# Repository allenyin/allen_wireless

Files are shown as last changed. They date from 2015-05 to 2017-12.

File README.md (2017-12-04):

**Wireless Neural Recording System**

* [Overview](#Overview)
* [Hardware](#Hardware)
	* [Steps to convert old KiCad design files](#convertKiCad)
	* [Bridge](#Bridge-hw)
	* [Headstages](#headstages)
* [Firmware](#Firmware)
	* [Dependency](#Firmware-dependency)
	* [Bridge](#Bridge-fw)
	* [RHA-headstage](#RHA-fw)
	* [RHD-headstage](#RHD-fw)
		* [Firmware versions](#firmware-versions)
		* [JTAG testing](#JTAG-testing)
		* [Utility Programs](#Utility-programs)
* [Client Software](#gtkclient)
	* [Dependency](#gtkclient-dependency)
	* [Compilation](#gtkclient-compile)
    * [Running gtkclient](#running-gtkclient)
        * [RHA-headstage gtkclient](#RHAgtkclient)
        * [RHD-headstage gtkclient](#RHDgtkclient)
        * [Spike sorting](#SpikeSorting)
        * [Saving recordings](#SavingRecordings)
        * [Test recording](#TestRecording)
        * [Configuration files](#gtkclientConfigurations)
	* [TODO/possible improvements](#gtkclient-TODO)
* [Quick Start](#quickstart)

## <a name="Overview">Overview</a>
This project is modified from the multi-branch of the wireless neural recording system of the [myopen project](https://github.com/tlh24/myopen/tree/multi) by Tim Hanson.

As summarized in Hanson's [thesis](http://m8ta.com/tim/dissertation.pdf), the original system 

>consists of digitizing headstages, receiver/ethernet bridge, and PC client software. Each headstage has 4 32-channel Intan analog amplifiers, and ADCs to digitize the amplified signals. The amplifiers are connected to an onboard Blackfin DSP BF532 which performs automatic gain control, LMS adaptive noise cancellation, 8 poles of high and lowpass filtering, two templates comparison per channel, data compression, and pipelined radio control. The radio onboard transmits 1.3Mbps full filtered analog trace of four channels and threshold/template match for two units on all 128 channels. This is interleaved with 83kbps reception,which allows the client to edit parameters on the transceiver. The radio protocol allows any memory location to be changed on the headstage (specifically the blackfin), and the headstage streams can stream from any location in memory, with the memory address set by the PC client.

[32-channel Intan analog amplifiers](http://intantech.com/products_RHA2000.html)

[Blackin DSP BF532](http://www.analog.com/en/products/processors-dsp/blackfin/adsp-bf532.html)

The bridge, which is based around [Blackfin DSP BF537](http://www.analog.com/en/products/processors-dsp/blackfin/adsp-bf537.html), collects the wirelessly transmitted data from the headstages and send them to the PC client through ethernet.

<a name="figure_overview">*System overview, from Hanson's [thesis](http://m8ta.com/tim/dissertation.pdf)*</a>
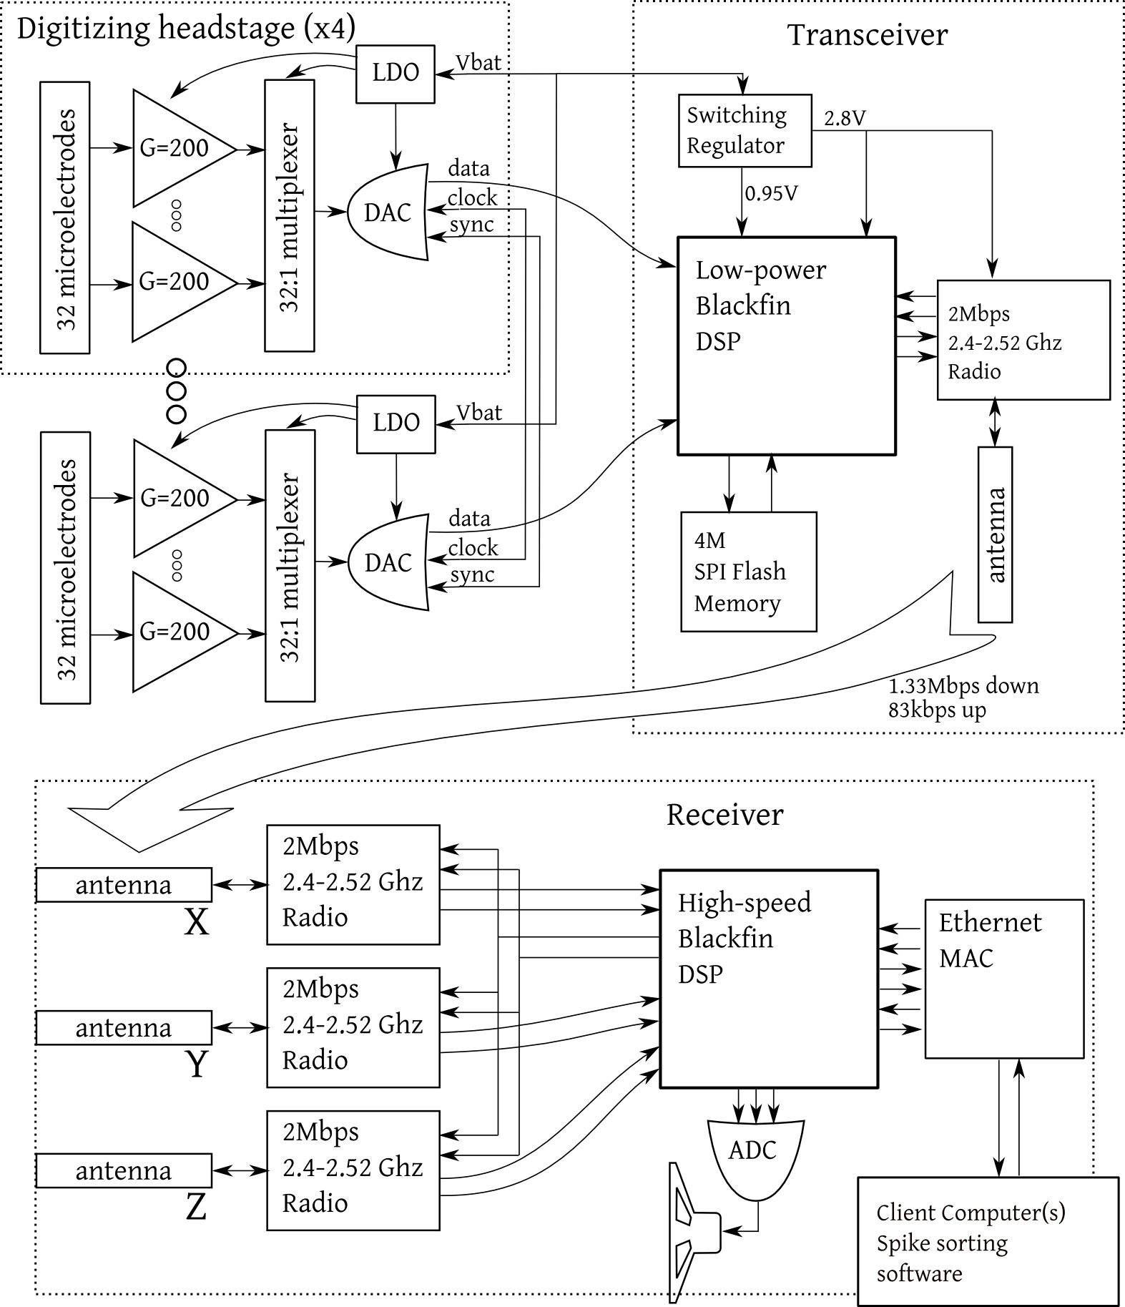
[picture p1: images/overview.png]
Hanson_Overview


This project modified the wireless headstage by replacing each of the 4 RHA2132 amplifiers, ADCs, and power converter chips with a single [32-channel RHD2132 digitizing amplifier](http://intantech.com/products_RHD2000.html). This is to reduce the power consumption and total area of the final PCB (by about 1/3). In terms of the figure above, this is equivalent of replacing the `G=200 and 32:1 multiplexer`, `ADC` and `LDO` components in the `Digitizing headstage` blocks by one component. 

In the rest of this document, the original headstages will be refered to as **RHA-headstage**, while the new design will be referred to as **RHD-headstage**. The client software will be referred to as **gtkclient**.

This document will describe:

* The overall hardware architecture of the headstages.
* Usage and setup for the bridge, headstage, and the PC client software.
* The different firmware versions used to develop and test the RHD-headstage.
* Debugging tools.

For technical details on the implementation, development, and troubleshooting of the firmware, see Tim's thesis, and the following development notes:

1. [Wireless Headstage: Blackfin BF532 headstage firmware setup](http://allenyin.github.io/reading_list/2016/01/BlackfinSetup)
2. [Wireless Headstage: Blackfin BF532 communication with Intan RHD2132 via SPI simulation via SPORT](http://allenyin.github.io/reading_list/2015/12/Blackfin-Intan-SPORT)
3. [Wireless Headstage: AGC with Blackfin BF532 and Intan RHD2132](http://allenyin.github.io/reading_list/2015/12/WirelessAGC)
4. [Wireless Headstage: Least-Mean Squared (LMS) adaptive noise cancellation](http://allenyin.github.io/reading_list/2016/01/BlackfinLMS)
5. [Wireless Headstage: Implementing direct-form I biquad IIR filters](http://allenyin.github.io/reading_list/2016/01/DirectFormI-IIR-butterworth-filters)
6. [Wireless Headstage: Generate oscillations by setting IIR coefficients](http://allenyin.github.io/reading_list/2016/01/IIRoscillator)
7. [Spike sorting via PCA and spike detection with SAA](http://allenyin.github.io/reading_list/2016/01/BlackfinSpikeSorting)
8. [Wireless Headstage: Radio transmission protocol between headstage and gtkclient](http://allenyin.github.io/reading_list/2016/01/BlackfinRadioTrans)
9. [Wireless Headstage: gtkclient notes](http://allenyin.github.io/reading_list/2016/01/gtkclient)

This repository contains the following folders:

* `bridge_hardware`: Ported from myopen's [stage10](https://github.com/tlh24/myopen/tree/master/emg_dsp/stage10). Components  stored in `bridge_library/`. Footprint archived to `bridge_library.pretty/` to use with newer version of `kicad (Version:0.201506030104+5696~23~ubuntu14.04.1-product,release build)`.

* `headstage_hardware`: Ported from myopen's [stage9](https://github.com/tlh24/myopen/tree/master/emg_dsp/stage9). Components stored in `headstage_library/`. Footprint archived to `headstage_library.pretty/` to use with newer version of kicad.

* `headstage2_hardware`: Modified from myopen's [stage9](https://github.com/tlh24/myopen/tree/master/emg_dsp/stage9). Uses 4xRHD2132 amplifiers rather than 4xRHA2132 amplifiers front-end. Eliminated separate ADCs and analog power-supply components.

* `myopen_multi`: Firmware and gtkclient software, which includes:
    * `bridge_firmware`: Same as myopen's [firmware_stage7](https://github.com/tlh24/myopen/tree/mutli/firmware_stage7).
    * `headstage_firmware`: Firmware for RHA-headstage. Port from myopen's [firmware_stage9_tmpl](https://github.com/tlh24/myopen/tree/multi/firmware_stage9_tmpl). Uses templates matching to transmit spike timings from the headstage.
    * `headstage2_firmware`: Firmware, development and debugging files for RHD-headstage.
    * `gtkclient_multi`: gtkclient source code adapted from myopen. Makefile modified to compile on Ubuntu14.04 and to support working with RHD-headstage's firmware.
    * `flasher`: Code used to write to the flash memories of the bridge and headstage through the parallel port.
    * `common_bfin`: Code common to all firmware and gtkclient.
    * `common_host`: Code common to the bridge firmware and gtkclient.
    * `algs`: Utilities need by gtkclient.
    
---
## <a name="Hardware">Hardware</a>

## <a name="convertKiCad">Steps to convert old KiCad design files</a>
The bridge and RHA-headstage PCB were designed with Tim's [kicadocaml](https://github.com/tlh24/kicadocaml), a variant of the opensource [KiCad](http://kicad-pcb.org/) PCB cad program. The design files were ported to KiCad, however the recent changes in KiCad's EESchema introduces some problems in using projects created with older version out of the box. Those impacts include:

0. Updated device library. The new device library footprints are smaller, this can cause older schematics to be displayed with broken connections. Solution: follow the procedures outlined [here](https://lists.launchpad.net/kicad-developers/msg17639.html) to use the rescue-lib.
0. Saving the old .brd files will convert them to .kicad_pcb. Subsequent openning of the board files will then result in parse errors and no board. Solution: Never save!!! (have not yet found a good solution).

In general, the KiCad files in `bridge_hardware/` and `headstage_hardware/` are for reference only, no save/modification should be needed.

The following steps were used to convert the old project files (example using `headstage_hardware/`):

0. Extract stage9 from `/emg_dsp`.
0. Create component and footprint library folders. `cd headstage_hardware; mkdir headstage_library headstage_library.pretty`
0. Open the schematic file, press OK for the rescue components dialog. Copy the cached component to our newly created library: `cp stage9-cache.lib headstage_library/headstage.lib`
0. Go to *Preferences*->*Component Libraries* and add headstage as an active library.
0. Ctrl-E on any of the component to open library editor. Set active library to be *headstage* and save component.
0. Close schematic and open again. Now editing any of the components in the library editor should show the active library as *headstage.lib*
0.  **Important! When closing the schematic, do not click on save!**
0. Open the .brd file, click ok on the resulting dialog.
0. Ctrl-E on any of the footprint to open the footprint editor. Click on *Create new library and save footprint* from the menu bar, and select the *headstage_library.pretty* folder to store the new library.
0. Go to *Preferences*->*Footprint libraries Wizard*->*Files on my computer* and select the *headstage_library.pretty* folder. This will add that directory to the footpring libraries available in this project. Make sure to select avaliable to project only.
0. *Select active library* in the footprint editor and make it *headstage_library.pretty*.
0. Close footprint editor and go back to the board. Go to *file*->*Archive Footprints*->*Create footprint archive* and select *headstage_library.pretty* as the library. Click yes to replace library. Now *headstage_library.pretty/* contains all the footprint used in the board as .mod files.
0. Make sure when footprint editor is opened, the active library is set correctly to the one we just created.
0. Again remeber to **NOT save the board file!!**
0. Open the schematic file and run Cvpcb to associate the components and the footprints in our own custom libraries. It's possible that a footprint is found in multiple libraries, chose to associate with the ones in *headstage*.

## <a name="Bridge-hw">Bridge</a>
As illustrated by the [Receiver block in the system overview](#figure_overview), the bridge mainly consists of three antenna-2.4GHz radio pairs for wireless communication, Blackfin DSP for processing, Ethernet/MAC chip for communication with gtkclient, and DAC (typo of DAC in Tim's thesis) for outputting received neural signals as audio.

In addition to wireless communication with the headstages, the bridge is also needed to program and debug the headstages.

<a name="bridge_labeled">*Bridge Board* </a>

labeled_bridge

In the above image:

A. Power switch.

B. USB power cable. 

C. Ethernet cable. Each operating headstage requires a bridge, requiring the PC on which gtkclient operates on to be connected to multiple bridges. Therefore, the ethernet port of the bridges and the client PC should all connect to the same switch or router.

D. Audio jack. When gtkclient is running, connecting the bridge to an audio device allows the user to hear the the 4 selected channels in gtkclient.

E. Blackfin BF537 DSP processor.

F. JTAG header pins for debugging the bridge. The pin missing on the top row ensures correct orientation of the JTAG in-circuit emulator (ICE).

G. Header pins for writing firmware to the bridge's flash memory. See [bridge flashing instructions](#Bridge-fw).

H. Indicator LED lights. After power on, these LEDs would fluctuate. Normal operation is indicated by the LEDs lit up in the image lighting up. Except for the bottom most one, which should be blinking periodically.

I. Header pins for writing firmware to the headstage's flash memory. See [RHA-flashing instructions](#RHA-fw) and [RHD-flashing instructions](#RHD-fw).

J. Omnetics connector for writing firmware to the headstage's flash memory. The signals applied to the column of header pins above it are applied to the headstage through this connection to the corresponding omnetics connector on the headstage.

K. JTAG header pins for debugging the headstage. The pin missing on the left column ensures correct orientation of JTAG ICE. See [RHD firmware testing](#JTAG-testing).

L. Omnetics connector for JTAG debugging the headstage. The signals applied to the JTAG header pins are passed to the headstage through this connection.

M. 2.4GHz Nordic radio and antenna pairs. Having three antenna allow for spatial reception diversity and enable better wireless signal quality.

**Parallel Port Flash Cable**

A 25-pins [IBM PC-comptabile parallel port](https://en.wikipedia.org/wiki/Parallel_port#Pinouts) cable is modified to use for the flashing process, see [firmware section](#Firmware) for instructions.  The unmodified end of the DB25 cable is connected to the parallel port, while the modified end connects to the 7-pin header connectors on the bridge, labeled G and I above.

The flash cable on one end needs to be modified as shown below:

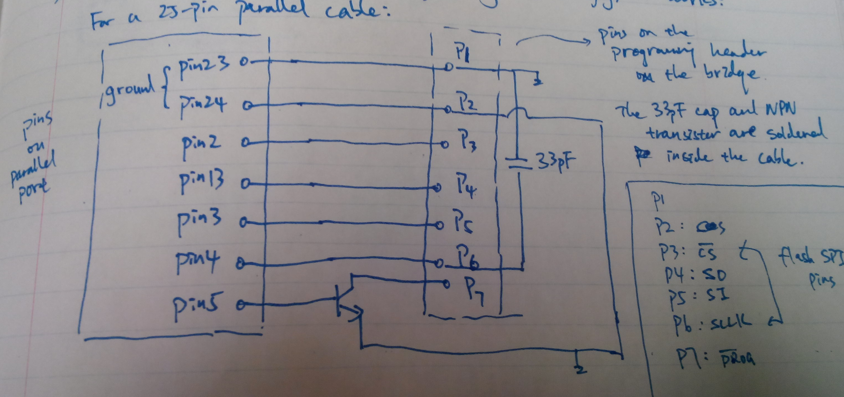
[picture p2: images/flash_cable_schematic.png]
flash_cable
<a name="flash_cable">*Flash Cable Schematic*</a>

The left box shows the relevant pins on the unmodified DB25 connector, the right box shows the corresponding header pins on the bridge. There needs to be a `33pF` capacitor connecting `pin23` and `pin4` of the parallel cable. `pin5` of the cable needs to connect to the base of an NPN transistor, whose emmiter is connected to ground via either `pin23` or `pin24`, while the collector goes to `pin7` of the bridge headers.

Specifically, the parallel port to SPI correspondence is:

* `pin2` = `_CS` -- chip select of the SPI flash memory.
* `pin13` = `SO` -- the input of the parallel port is connected to the output (SO) of the flash memory.
* `pin3` = `SI` -- the output of the parallel port is connected to the input (SI) of the flash memory.
* `pin4` = `SCLK` -- serial clock (SCLK) of the flash memory.

`pin5` is not part of the 4-line SPI interface, but it is used to allow the line-driver onboard the bridge to select the flash memory to use the SPI bus. This is necessary since the SPI bus on the Blackfins of both the bridge and headstage is shared between the flash memory and the radio chip.

The modified flash cable will include the capacitor and the NPN transistor. The polarity of the 7-pin connector can be figured out by probing to see which pin is grounded onboard the bridge.

## <a name="headstages">Headstages</a>

In image below, the fully assembled RHA-headstage is on the left. The RHD-headstage is on the right.

<a name="headstages_labeled">*Headstage PCBs*</a>

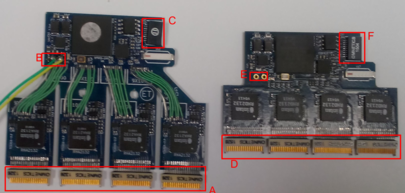
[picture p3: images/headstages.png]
labeled_headstages labled_headstages


Labeled in the image are the connectors the headstages can make:

A. RHA-headstage Omnetics connectors to electrodes. Each of the four connectors has two rows of 20 pins each. The leftmost and rightmost pins of each row are guide posts and connect no signals. The second leftmost and the second rightmost pins of each row are the reference electrodes.

B. RHA-headstage power connection to 3.7V battery.

C. RHA-headstage Omnetics connector for flashing memory. The JTAG debugging connector is on the back side of the board at the same location.

D. RHD-headstage Omnetics connectors to electrodes. Exactly the same as the RHA-headstage.

E. RHD-headstage power connection to 3.7V battery. Connection not installed in the pictre.

F. RHD-headstage Omnetics connector for flashing memory. The JTAG debugging connector is on the back side of the board at the same location.

The bottom half of both headstages are the `digitizing headstages` block in the [System overview diagram](#figure_overview), which is where the headstages differ hardware-wise. The top halves are the `transceiver block` and are identical.

While the electrodes for both headstages are identical, the electrode-to-amplifier connections are different. Below are the electrode-to-channel mapping for each headstage, containing only the 32 signal-carrying electrodes of the connector (excluding the guide posts). Note that each amplifier is connected to one group of 32 electrodes.

*RHA-headstage electrode-to-channel mapping, ordered from left-to-right*

top-row|31|30|29|28|27|26|25|24|23|22|21|20|19|18|17|16|
-------|---|---|---|---|---|---|---|---|---|---|---|---|---|---|---|---|
bot-row|15|14|13|12|11|10| 9| 8| 7| 6| 5| 4| 3| 2| 1| 0|

*RHD-headstage electrode-to-channel mapping, ordered from left-to-right*

top-row|23|22|21|20|19|18|17|16|15|14|13|12|11|10|9|8|
-------|---|---|---|---|---|---|---|---|---|---|---|---|---|---|---|---|
bot-row|24|25|26|27|28|29|30|31|0|1|2|3|4|5|6|7|

## <a name="Firmware">Firmware</a>
The firmware is written in a combination of C and Blackfin assembly language. While Analog Devices (ADI) provides its own software development toolchains, it requires purchasing a pretty expensive license (though it comes with a lot more support). For the myopen and this project, the open source gnu gcc blackfin toolchain is used. Further, all development was done on debian based OS. The Makefiles in this repository are tested only in Ubuntu 14.04. Minor adjustments might be needed to work on other debian-based OS.

## <a name="Firmware-dependency">Dependency</a>

Compiling the firmware requires the [Blackfin Toolchain in Linux for Bare Metal](https://blackfin.uclinux.org/doku.php?id=toolchain:installing). For debian-based linux OS:

* Download the latest version, as of June, 2015, it's `blackfin-toolchain-elf-gcc-4.3-2014R1-RC2.x86_64.tar.bz2`
* Extract and move to `/opt`
* Add path to `/opt/uClinux/bfin-elf/bin` to the `PATH` variable through `.bashrc`

Two must-have references to understand Blackfin architecture:

* [ADSP-BF5xx/ADSP-BF60x Blackfin Processor Programming Reference](http://www.analog.com/media/en/dsp-documentation/processor-manuals/Blackfin_pgr_rev2.2.pdf), describes all assembly commands and options.
* [ADSP-BF533 Blackfin Processor Hardware Reference](http://www.analog.com/media/en/dsp-documentation/processor-manuals/ADSP-BF533_hwr_rev3.6.pdf), describes all components and functions of the processor.  BF533 processor is mostly identical with BF532, which are the processors onboard the headstages. For the bridge, see BF537.

After compiling the firmware, the binary needs to be uploaded into the SPI flash memory onboard the bridge or headstage. This is done through a parallel port (for speed and relative ease). There are two ways this could be done.

**Using Libparapin**

In older computers with integrated parallel port (such as our lab's `rabbit` running DebianWheezy), [libparapin](http://parapin.sourceforge.net) can be installed to talk to the paralle port. This was used by Tim to develop and flash the RHA-headstages.

After installation of libparapin (in either user or kernel mode), compile `myopen_multi/flasher/flash.c` with `make clean; make`. 

With proper PC-to-bridge (and bridge-to-headstage) connections, compiled firmware binary can be uploaded with `sudo ./flash myprogram.ldr`.

**Using Pyparallel (recommended)**

Unfortunately Libparapin does not play nicely with parallel port PCI expansion cards and/or newer OS. I'm not sure what the exact culprit is, but the most recent version of libparapin is for kernel version2.6, and there hasn't been any activity on the project in several years.

Fortunately the python library [pyparallel](https://github.com/pyserial/pyparallel), allows us to interact with the parallel conveniently. Note that `pyparallel` can also refer to a Python parallel processing package. See [Lewis Loflin's blog posts](http://www.bristolwatch.com/pport/index.htm) for details on using the library.

After installing this module, firmware can be flashed with `python flash.py myprogram.ldr`. Error might occur indicating parallel port cannot be openened, in which case do `sudo rmmod lp; sudo modprobe ppdev` and try again.

Successful flash message:
```
python ../flasher/flash.py stage.ldr
ldr file: stage.ldr
File size 12202 bytes, 48 pages.

Requesting manufacturer opcode...

Read: 0xbf 

Looks like microchip flash.
Read: 0xbf 

Read: 0x25 

Read: 0x8d 

Read: 0xbf 

Detected: 
SST25VF040
SST25 sanity check ok.
Status register 0x0
Bank protect bits = read-write.
AAI off.
Block protect off.
Device is not write enabled. (default)
Device is ready.
Erasing SST25!
Waiting for the erase to complete..
Status register 0x0
Bank protect bits = read-write.
AAI off.
Block protect off.
Device is not write enabled. (default)
Device is ready.
write_all2_SST25 writing buffer length 12202
Verifying all..
 ok.

All pages verified correctly! :)
```
## <a name="Bridge-fw">Bridge</a>

The bridge firmware was not modified from the original myopen project (except the Makefile, for directory consistency). To flash the bridge, connect the flash cable to the bridge header pins as below, note the direction of cable connection is marked on the red flash cable.

<a name="Bridgeflash">*Flashing the bridge*</a>
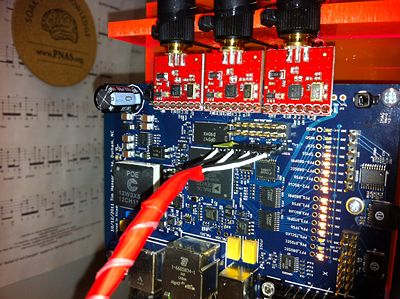
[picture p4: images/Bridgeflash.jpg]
Bridgeflash


1. Go to the `myopen_multi/bridge_firmware/` directory, and do `make clean; make` to compile the firmware. 

	Note that each bridge is receives from a different headstage. Therefore, if multiple headstages are used, multiple bridges will need to be flashed and used. 

	If multiple briges are used, make sure the MAC addresses for the bridges are different. Go to `myopen_multi/common_bfin/ethernet.c`, in function `SetupMacAddr()`, change the value of `MACaddr[5]` so that the bridges used have different values.

2. Turn the bridge on, making sure the USB power cable is connected, then do `make flash`. 
 
	`make flash` will use either the libparapin based `flash.c` or pyparallel based `flash.py` to write the firmware to memory, based on what option is enabled in the Makefile under the `flash` rule. The default option will use the Python method.

## <a name="RHA-fw">RHA-headstage</a>

The RHA-headstage firmware was not modified from the original myopen project (except the Makefile, for directory consistency). To flash the heastage, connect the flash cable to the bridge header pins, and the 9-pins Omnetics cable to the bridge as shown below, note the direction of cable connection is marked on the red flash cable.

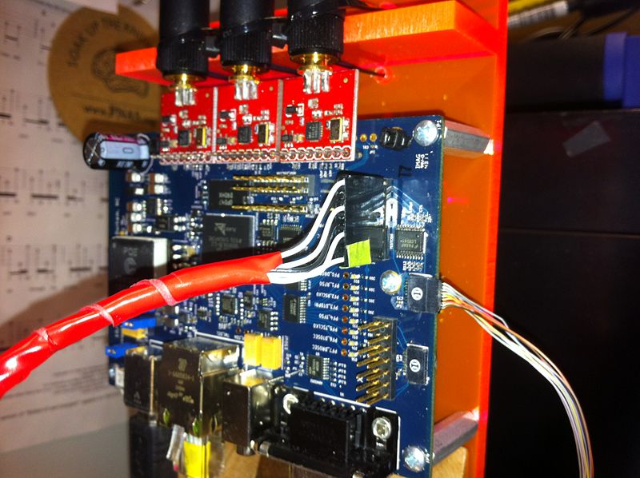
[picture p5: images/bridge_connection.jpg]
bridge_connection
<a name="bridge_connection">*Bridge connection to flash headstage*</a>

1. Connect the other end of the 9-pins cable to the top-side omnetics connector on the headstage as shown below, note that the top wire on the bridge is also the top wire on the headstage.

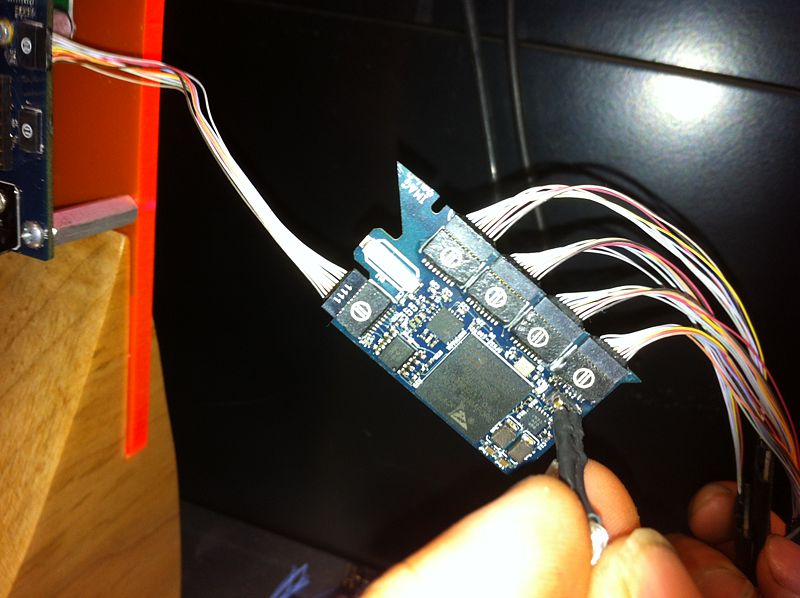
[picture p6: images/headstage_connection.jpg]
headstage_connection
	<a name="headstage_connection">*RHA-headstage connection*</a>

	Note that the RHA-headstage shown in the image is only the transceiver top half.

2. Go to the `myopen_multi/headstage_firmware/` directory, and do `make clean; make` to compile the firmware.

	Note that if multiple headstages are used, they must be configured to operate on different radio frequency. To change the radio channel, go to `myopen_multi/headstage_firmware/main.c` and search for the call to `radio_init()` and change the input argument. An input value of `84`, for example, sets the radio to operate on `2400MHz + 84Hz = 2484Mhz`. Other possible values are 94, 114, and 124. The maximum is 124. These changes must be followed by firmware recompilation.

    Theoretically, the 2.4GHz radio used onboard can operate with 2Msps on 62 different 2MHz bandwidth channels. The radio can operate from 2.4GHz to 2.525Ghz. When operating at 2Msps, each frequency requires a 2MHz bandwidth. Therefore, with no overlap, the input value to `radio_init()` can take values of 0, 2, 4,..., 124. However, the lower frequency bands are prone to attenuation by water absoprtion and interference from WiFi/Bluetooth/ZigBee bands. Therefore, the actual frequencies used should be limited to the higher bands. When multiple headstages are used, they should be set at frequencies as far apart as possible (note the separation of 10-20MHz for the values suggested).

    See [Nordic nRF24L01 manual section6.3](http://www.nordicsemi.com/eng/content/download/2730/34105/file/nRF24L01_Product_Specification_v2_0.pdf).

3. Turn on the bridge, and flash the headstage with `make flash`. 

	`make flash` will use either the libparapin based `flash.c` or pyparallel based `flash.py` to write the firmware to memory, based on what option is enabled in the Makefile under the `flash` rule. The default option will use the Python method.

4. Modify gtkclient:
 	* Make sure in `myopen_multi/gtkclient_multi/Makefile`, the option `HEADSTAGE_TIM` is set to `TRUE`, while setting `RADIO_BASIC`, `RADIO_AGC`, `RADIO_AGC_IIR` and `RADIO_AGC_IIR_SAA` to `false`.
	* Go to `myopen_multi/gtkclient_multi/src/gtkclient.cpp` and make sure the radio channel given to `radio_init()` in the headstage's firmware is present in the array `g_radioChannel`. 
	* If using multiple headstage-bridge pairs for recording, make sure the value of `NSCALE` defined in `myopen_multi/gtkclient_multi/include/gtkclient.h` is set to the number of headstage-bridge pairs used.
   
    After all (if any) gtkclient modifications, recompile gtkclient by navigating into `myopen_multi/gtkclient_multi` and type `make clean; make`. gtkclient is now ready to be used with RHA-headstages.

When powered on, the LED onboard should blink periodically.

The file `memory_map.ods` is a spreadsheet visualizing the memory organization used in the RHA-headstage firmware.

## <a name="RHD-fw">RHD-headstage</a>

The parallel port-to-bridge connections and bridge-to-headstage connections are identical for RHD-headstage as for RHA-headstages. However, there are multiple firmwares available in the `myopen_multi/headstage2_firmware` directory. To program the RHD-headstage to use the final firmware version -- `radio_gain_IIR_SAA.asm`, navigate to that directory and:

1. Uncomment the line `FIRMWARE_VERSION=radio_gain_IIR_SAA` line in `myopen_multi/headstage2_firmware/Makefile`.

2. Type `make clean; make` to compile the firmware.

	Note that if multiple headstages are used, they must be configured to operate on different radio frequency. To change the radio channel, go to `myopen_multi/headstage_firmware/main.c` and search for the call to `radio_init()` and change the input argument. An input value of `84`, for example, sets the radio to operate on `2400MHz + 84Hz = 2484Mhz`. Other possible values are 94, 114, and 124. The maximum is 124. These changes must be followed by firmware recompilation.

    Theoretically, the 2.4GHz radio used onboard can operate with 2Msps on 62 different 2MHz bandwidth channels. The radio can operate from 2.4GHz to 2.525Ghz. When operating at 2Msps, each frequency requires a 2MHz bandwidth. Therefore, with no overlap, the input value to `radio_init()` can take values of 0, 2, 4,..., 124. However, the lower frequency bands are prone to attenuation by water absoprtion and interference from WiFi/Bluetooth/ZigBee bands. Therefore, the actual frequencies used should be limited to the higher bands. When multiple headstages are used, they should be set at frequencies as far apart as possible (note the separation of 10-20MHz for the values suggested).
	
    See [Nordic nRF24L01 manual section6.3](http://www.nordicsemi.com/eng/content/download/2730/34105/file/nRF24L01_Product_Specification_v2_0.pdf).

3.  Turn on the bridge and do `make flash`. 

	There should be a line in the output message that says `FIRMWARE_VERSION is RADIO_GAIN_IIR_SAA`. If not, make sure again in Makefile that all other lines containing `FIMRWARE_VERSION=` is commented out.

4. Modify gtkclient:
	* Go to `myopen_multi/gtkclient_multi/Makefile` and set the option `RADIO_GAIN_IIR_SAA` to true, while setting `HEADSTAGE_TIM`, `RADIO_BASIC`, `RADIO_AGC`, `RADIO_AGC_IIR`, `RADIO_AGC_IIR_SAA` to `false`. This ensures gtkclient can correctly communicate with the RHD-headstage firmware.
	* Go to `myopen_multi/gtkclient_multi/src/gtkclient.cpp` and make sure the radio channel given to `radio_init()` in the headstage's firmware is present in the array `g_radioChannel`.
	* If using multiple headstage-bridge pairs for recording, make sure the value of `NSCALE` defined in `myopen_multi/gtkclient_multi/include/gtkclient.h` is set to the number of headstage-bridge pairs used.

	After all (if any) gtkclient modifications, recompile gtkclient inside `myopen_multi/gtkclient_multi` directory with `make clean; make` -- gtkclient is now ready to be used with RHD-headstage.

When turned on, the onboard LED should blink periodically.

## <a name="firmware-versions">Firmware versions</a> ##
There are other firmware version in this directory, many of them were used in the process and developing
the final firmware.

* `intan_setup_test.asm`:  

    Polls the same channel from all 4 Intan amplifiers, and save periods to memory starting at FP_BASE (0xFF906F00). Plot the result using `plot_memdump.py`, function `within_amp()`. Used to find optimal setup for the RHD amplifiers.

    Compile and flash with `make clean; make; make flash` after uncommenting `FIRMWARE_VERSION=intan_setup_test` and commenting out all other `FIRMWARE_VERSION` comments. Does not use the radio so not supported by gtkclient.

    The blackfin cache memory organization can be visualized by the spreadsheet `Intan_setup.ods`. Memory header is `memory_RHA.h` -- identical to RHA-headstage's `memory.h` file.

* `intan_setup_test2.asm`: 

    Tests the intra-amp performance. Records a set number of periods from all 32 channels of a fixed amp (see comments in file), save to memory in A1 (0xFF904000). Results include Intan-setup responses. Use `plot_memdump.py`, function `within_amp()` to plot the results.

    Compile and flash with `make clean; make; make flash` after uncommenting `FIRMWARE_VERSION=intan_setup_test2` and commenting out all other `FIMRWARE_VERSION` comments. Does not use the radio, not supported by gtkclient.

    The blackfin cache memory organization can be visualized by the spreadsheet `Intan_setup.ods` Memory header is `memory_RHA.h` -- identical to RHA-headstage's `memory.h` file.

* `firmware1.asm`:
   
    Integrated intan_test_setup2 into the firmware structure...after the setup process, repeatedly poll all the SPORT, but saves all channels from just one amp to WF_BUF. This allows for 256 32-bit words, which is equivalent to getting 16 samples from all 32-channels of the designated amplifier. 

    After saving the samples, part of the signal chain (AGC+IIR+SAA) was used to see how much code-path can be fit in before data corruption happens. The data in WFBUF can be dumped after it's full and plotted with `plot_packet_samples.py` (`plot_packet('bla.txt', 16, 32)`). Contains no radio code. Not supported by gtkclient.

    Memory header is `memory_RHA.h` -- identical to RHA-headstage's `memory.h` file.

* `firmware2.asm`:

    Same as `firmware1.asm`, except the extra signal path code is replaced with nops to investiage code-length issues.

* `radio_basic.asm`:

    Built off firmware2.asm, but integrate in radio communication with gtkclient. The radio communication involved is a stripped-down version of the original radio protocol -- writes in the raw samples, but since no spike-sorting is done, the matching bits are simply set to 0. Instructions to add in the echo nibble and packet#-in-frame nibble are present, so gtkclient can correctly read and interpret the packet information. 
                 
    Requires uncommenting the `FIRMWARE_VERSION=radio_basic` in makefile to compile, uses the "memory_radio_basic.h" file, which describes the memory layout. The memory header file is taken care of by the Makefile. The corresponding header will be moved to be "memory.h" when the `FIMRWARE_VERSION` option is set.

    The blackfin cache memory organization can be visualized by the spreadsheet `radio_basic_memoryMap.ods`.

    To use with gtkclient, compile gtkclient with `RADIO_BASIC` set to true in the Makefile. 

    While running gtkclient, since no matches are actually made, in the spike-window, the waveforms may be colored blue and messages in stdin about false-positivies can happen. This is normal and safe to ignore.

* `radio_AGC.asm`:

    Built off radio_basic.asm, but with added AGC functions. Same radio-communication protocol as in radio_basic. Compile with `FIMRWARE_VERSION=radio_AGC`, use "memory_AGC.h". 

    The blackfin cache memory organization can be visualized by the spreadsheet `radio_AGC_memoryMap.ods`.

    To use with gtkclient, compile gtkclient with `RADIO_AGC` set to true in its Makefile. Same spike false-positives will occur.

* `radio_AGC_IIR.asm`:

    Built off radio_AGC.asm, but added two IIR biquads to act as band-pass filter, set to [250, 9000Hz]. Compile with `FIMRWARE_VERSION=radio_AGC_IIR`, use "memory_AGC_IIR.h".

    The blackfin cache memory organization can be visualized by the spreadsheet `radio_AGC_IIR_memoryMap.ods`.

    To use with gtkclient, compile gtkclient with `RADIO_AGC_IIR` set to true in its Makefile. Same spike false-positives will occur.
                   
    <s>Note that unlike the original gtkclient, this version will not have an option to set the gain. This is because previously the samples were 12-bits, with Q16 values, the IIR may adjust its coefficients to apply a gain of up to 2 on its incoming samples, this is the mechanism through which Tim's gtkclient applies the gain. In the RHD version of headstage, the incoming samples are already 16-bits, therefore no gain needs/should be applied.</s> 
    
    The `IIR-gain` field allows an extra gain to be applied via the low-pass biquad. In practice, this should limitied between [-2.5, 2.5]. See [Wireless Headstage: Implementing direct-form I biquad IIR filters](http://allenyin.github.io/reading_list/2016/01/DirectFormI-IIR-butterworth-filters) for details. This is the case for all RHD firmware containing AGC and IIR stages.
                   
    By changing the IIR-biquad coefficients, oscillations of different frequency may be introduced. The `osc` radio button in this version of gtkclient does this. Clicking that radio button sets the IIR coefficients of the selected channels so the final IIR outputs oscilate at 250Hz. Clicking the `250-9000Hz` radio button restores the bandpass filtering behavior on the selected channels. This may serve as a good test for radio operation.

* `IIR_oscillator_test.asm`: 
   
    Used to test IIR-based oscillator. Basically is radio_AGC_IIR.asm without the radio transmission code in the main thread, or the radio_loop code. Sets up initial conditions on the biquads and their coefficients. 
                        
    Save 68 samples each for 32 channels on a single amp (or different, can be changed in code) to memory at 0xff806300. JTAG running and dumping the memory can visualize the resulting waveform. Visualize using plot_memdump.py, `within_amp_32ch()`. Used to confirm the biquad oscillation coefficients.

* `radio_AGC_IIR_SAA.asm`:   

     Adding the spike-sorting using SAA instructions to radio_AGC_IIR.asm. <s>This is the final firmware for RHD headstages</s>. Compile with `FIRMWARE_VERSION=radio_AGC_IIR_SAA`, uses "memory_AGC_IIR_SAA.h". 

     The blackfin cache memory organization can be visualized by the spreadsheet `radio_AGC_IIR_SAA_memoryMap.ods`.

     Edit on 4/5/2016 - Validation has shown that AGC makes spike sort harder when SNR is low. Therefore, this is no longer recommended as the final version for RHD-headstage.

* `radio_gain_IIR_SAA.asm`:

     The IIR and SAA parts of the signal chain are present in this version of the firmware. However, the AGC stage has been replaced by a manually set fixed-gain stage, the gain ranges from -128 to 127.5 in increments of 0.5. In gtkclient, this is the box labeled `preGain`. Compile with `FIRMWARE_VERSION=radio_gain_IIR_SAA`, uses "memory_gain_IIR_SAA.h".

    The blackfin cache memory organization can be visualized by the spreadsheet `radio_gain_IIR_SAA_memoryMap.ods`.

    <s>As of 4/5/2016, this is recommended as the final firmware version to be used on the RHD-headstage.</s>

* `radio_AGC_LMS_IIR_SAA.asm`:

    This version contains AGC, LMS, IIR, and SAA stage (the same signal chain as the RHA version), with the exception that the IIR stage contains only 1 LPF and HPF biquad). The LMS stage is incredibly useful for real recordings to reduce the noise and the IIR-gain can then amplifier the passband even more. LMS can be turned off via the setting in gtkclient. As of 7/26/2017, this is the preferred firmware version to use on the RHD-headstages.

    The blackfin cache memory organization can be visualized by `radio_AGC_LMS_IIR_SAA_memoryMap.ods`.

## <a name="JTAG-testing">JTAG testing</a>
Both RHD and RHA headstages have JTAG connectors that allows for in-circuit debugging. Documented here are the procedures for using the [gnICE debugger](https://docs.blackfin.uclinux.org/doku.php?id=hw:jtag:gnice-plus). 

After flasing the firmware you want to test onto the headstage, connect the 9-pin Omnetics connector labeled L on the [bridge](#bridge_labeled) to the 9-pin Omnetics connector on the back of the headstage.

Connect gnICE from PC USB port to the JTAG header pins labeled J on the [bridge](#bridge_labeled).

Turn on the bridge, in one terminal, type `bfin-gdbproxy -q bfin`, on successful detection of the debugger, the following message would appear:

```
Found USB cable: gnICE
Connected to libftdi driver.
IR length: 5
Chain length: 1
Device Id: 01100010011110100101000011001011 (0x627A50CB)
  Manufacturer: Analog Devices, Inc. (0x0CB)
  Part(0):      BF533 (0x27A5)
  Stepping:     6
  Filename:     /opt/uClinux/bfin-elf/bin/../share/urjtag/analog/bf533/bf533
warning:   bfin: no board selected, BF533 is detected
notice:    bfin: jc: waiting on TCP port 2001
notice:    bfin: jc:  (you must connect GDB before using jtag console)
notice:    bfin-gdbproxy: waiting on TCP port 2000
```
failed message such as:

```
Found USB cable: gnICE
Connected to libftdi driver.
warning: TDO seems to be stuck at 1
error:     bfin: detecting parts failed
Found USB cable: gnICE
error: Couldn't connect to suitable USB device.
error:     bfin: cable initialization failed
Found USB cable: gnICE
error: Couldn't connect to suitable USB device.
error:     bfin: cable initialization failed
```
Usually means the headstage-to-bridge JTAG connection is incorrect, or the bridge is not powered on.

After gnICE is detected, there are two ways to start a gdb debugging session. The first way is from terminal, do `bfin-elf-gdb stage.dxe`. Then in the `bfin-elf-gdb` prompt, type `target remote :2000` to connect to the gnICE. Successful connection would result in the following message in the gnICE terminal:

```
notice:    bfin-gdbproxy: connected
```
Debugging is then identical to using gdb.

The graphical debugger [Insight](https://www.sourceware.org/insight/) can also be used, and is recommended. A good manual for using Insight with blackfin can be found in section5.ch's [IceBear](http://www.section5.ch/dsp/icebear/ICEbear-manual.pdf) manual. IceBear is an alternative in-circuit emulator(ICE)/debugger for the blackfin, but has been discontinued.

To launch Insight, type `bfin-elf-insight stage.dxe`, should be able to connect to bfin-gdbproxy automatically. If not, in `File`->`Target Setting` chose the option `GDBServer/TCP` and for port enter `2000`.

As of version6.6, Insight may pop messages asking `Make breakpoint pending on future shared library load?` -- choose `no` on all of them. Error message saying `error: bad text index "4"` can also be safely ignored by clicking `ok`.

## <a name="Utility-programs">Utility Programs</a>

`myopen_multi/headstage2_firmware` also includes a number of utility programs used in the development and debugging process:

* `plot_memdump.py`, requires matplotlib, numpy and scipy.

    In JTAG debugging, memory values can be dumped when execution is paused. These values can then be processed and plotted. For example, while using `intan_setup_test2.asm`, with the following preprocessor setup:

    ```
    #define TESTFREQ                3200 // Hz
    #define STORAGE                 2480
    #define SAMPLE_PER_CH           150
    #define SAMPLE_PER_CH_MINUS_3   147
    #define TOTAL_CONVERT           4800   // 32*SAMPLE_PER_CH
    #define TOTAL_CONVERT_MINUS_3   4797
    ```

    and the subroutine `save_one_amp` as:
    
    ```
    save_one_amp:
        r1 = w[p0 + (SPORT1_STAT - SPORT0_RX)];
        cc = bittst(r1, 0);
        if !cc jump save_one_amp;

        // save new samples, in order from amp1 to amp4
        r2 = [p0 + (SPORT1_RX - SPORT0_RX)];    // SPORT1 pri - 2nd amp
        r3 = [p0 + (SPORT1_RX - SPORT0_RX)];    // SPORT1 sec - 1st amp
        r2 >>= SHIFT_BITS;
        r3 >>= SHIFT_BITS;
        //w[p1++] = r3;                           // save 1st amp
        //w[p1++] = r2;                           // save 2nd amp

        r2 = [p0];                              // SPORT0 pri - 4th amp
        r3 = [p0];                              // SPORT0 sec - 3rd amp
        r2 >>= SHIFT_BITS;                      
        r3 >>= SHIFT_BITS;
        w[p1++] = r3;                           // save 3rd amp
        //w[p1++] = r2;                           // save 4th amp
        rts;
    ```

    and setting a breakpoint at the line `jump we_finished`, when the execution is paused, we will have recorded 2472 32-bit words starting from memory location `A1` with the address `0xFF904000`. If we were applying a 3200Hz wave to some of the third group of electrodes, that would mean we have recorded 15 periods of that signal.

    In the gdb prompt of Insight debugger (or just the regular gdb prompt), we can dump the recorded signals (in addition to other setup values, see comments) to `gdb.txt` by:

    ```
    set logging redirect on
    set logging on
    x/2480xw 0xFF904000
    set logging off
    ```

    We can then plot the recorded values from all 32 channels of the 3rd group of electrodes in iPython with functions defined in this script:

    ```
    %run plot_memdump.py
    data = within_amp('gdb.txt', 32, 3200, 15)
    ```

    Below on the right is the plot result. Only 4 channels are actually applied the signal, the rest are grounded.

    <a name="JTAG1">*Using plot_memdump.py with intan_setup_test2*</a>
    
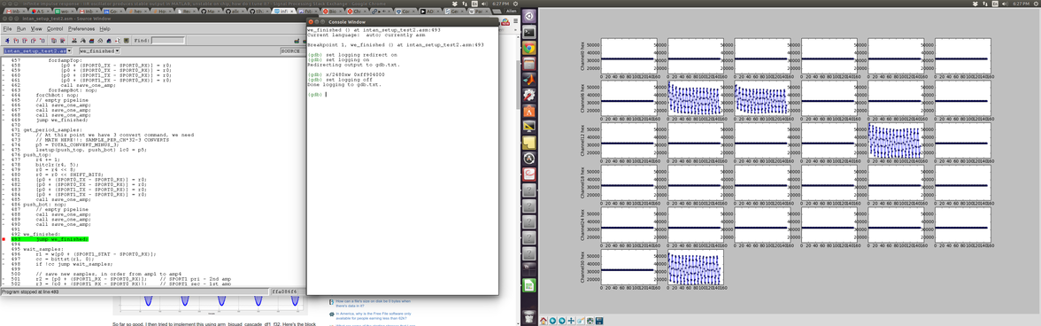
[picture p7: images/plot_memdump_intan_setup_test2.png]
JTAG1
    

    Use the function `within_amp_32ch()` for use with `IIR_oscillator_test.asm`.

    The function `saveCh_to_mat()` can convert the dumped gdb values as mat files, which can be imported into Matlab for analysis.

* `plot_packet_samples.py`

    Used with `firmware1.asm` and `firmware2.asm`. Saves samples from all 128 channels to WF_BUF, starting at memory location 0xff804000. Breakpoint should be set at `jump we_finished` in both files. At the end of execution, 256 32-bit words would be saved.

    The dumped values can then be plotted by `plot_packet_allChannels('gdb.txt')`.

* `fixedPointConvert.py`, `AGC_sim.py` contains functions that simulate the fixed-point conversion and arithmetic operations on Blackfin. 

    `AGC_sim.py` also contains simulates the AGC algorithm used in the headstage signal chain (see [AGC article](http://allenyin.github.io/reading_list/2015/12/WirelessAGC/) for details). Sample outputs of `AGC_sim.py` in iPython can be found in `AGC_sim_examples.txt`.

* `calc_memoryAddr.py` is used to confirm that given the different firmware version's memory file, gtkclient will be able to correctly calculate the relevant memory addresses.

    Even though all firmware is compiled with `memory.h`, it is actually a copy of either `memory_RHA.h`, `memory_radio_basic.h`, `memory_radio_AGC.h`, `memory_radio_AGC_IIR.h` or `memory_radio_AGC_IIR_SAA.h`. For example, to change the AGC target of a specific channel, the memory address to write the new value to in headstage running `radio_AGC.asm` is different from that running `radio_AGC_IIR.asm`. These memory address is calculated by gtkclient (specifically, in `myopen_multi/gtkclient_multi/src/headstage.cpp`) from the `memory.h` file generated by `headstage2_firmware/Makefile`.

    To use `calc_memoryAddr.py`, change the variables defined in the beginning of the file to match the corresponding firmware memory header file. Then run `setAGC(15)` for example to calculate what address gtkclient would output for changing the AGC target of channel 15. That address can then be verified against the `radio_AGC_memoryMap.ods`, for example, in the case of testing `radio_AGC.asm`.

## <a name="gtkclient">Client Software</a>

The client software, *gtkclient* is as summarized in Hanson's [thesis](http://m8ta.com/tim/dissertation.pdf)

> The sorting client is written in C/C++ using the GTK2 GUI toolkit with OpenGL and HLSL for graphics, [...] exclusively on Debian GNU/Linux. It consists of around 12600 lines of code, much for managing the GUI, displaying waveforms on the screen, maintaining persistent state, saving data, and communicating with [other] software clients [such as BMI3].

## <a name="gtkclient-dependency">Dependency</a>

Most of the dependency can be installed by going to `myopen_multi/gtkclient_multi` and run `make deps` and following the instructions.

Since gtkclient uses the GTK2 GUI toolkit, which may not be a default repository in newer linux distributions the user may have to edit the sources list or manaully download and install the packages. As of Ubuntu 14.04, this was not needed.

gtkclient also requires `nvidia-cg-toolkit`, it is recommended (if not mandatory) to run gtkclient on Nvidia graphics cards. Also, according to [NVIDIA](https://developer.nvidia.com/cg-toolkit)

>The Cg Toolkit is a legacy NVIDIA toolkit no longer under active development or support. Cg 3.1 is our last release and while we continue to make it avaiable to developers, we do not recommend using it in new development projects because future hardware features may not be supported.

gtkclient is known to work fine on `Nvidia GeForce GTX760/770/550 Ti`. 

On different Linux distros, the file path to `HDF5` and `libmatio` may be different. Compilation errors regarding these libraries can be fixed by giving the installed paths to them in [gtkclient's Makefile](https://github.com/allenyin/allen_wireless/blob/master/myopen_multi/gtkclient_multi/Makefile)(`HDF4INCLUDE`).

## <a name="gtkclient-compile">Compilation</a>

gtkclient can be compiled to work with both RHA-headstage and RHD-headstage, the latter of which may operate on multiple versions of firmware.

The deployment firmware versions is `myopen_multi/headstage_firmware/radio5.asm` for RHA-headstage, and `myopen_multi/headstage2_firmware/radio_gain_IIR_SAA.asm`.

Before compiling gtkclient to work with either RHA-headstage or RHD-headstage with the deployment firmware, one must:

* Match headstage numbers - make sure value of `NSCALE` set in `myopen_multi/gtkclient_multi/include/gtkclient.h` is equal to the number of headstages to be used.
* Match radio channels. 

    * First make sure the headstages to be used operate on different radio channels when flashing their firmware (see [RHA-headstage firmware section](#RHA-fw) and [RHD-headstage firmware section](#RHD-fw)) for instructions.
    * Make sure the radio channels of the headstages are present in the array `g_radioChannel` in `myopen_multi/gtkclient_multi/src/gtkClient.cpp`.

* Make sure if multiple headstages are used, the same number of bridges are used as well and connected to the PC running gtkclient through a switch or router. Also make sure the MAC address for each bridge is different, see [Bridge firmware section](#Bridge-fw) for instructions on this.

Then, if using RHA-headstage, go to `myopen_multi/gtkclient_multi` near the top of the file, set `HEADSTAGE_TIME=true` while setting `RADIO_BASIC=false`, `RADIO_AGC=false`, `RADIO_AGC_IIR=false`, `RADIO_AGC_IIR_SAA=false`, and `RADIO_GAIN_IIR_SAA=false`. Note that the options correspond to the different version of RHD-headstage firmware, with capitalization differences.

If using deployment firmware on RHD-headstage, go to `myopen_multi/gtkclient_multi` near the top of the file, set <s>`RADIO_AGC_IIR_SAA=true`</s> `RADIO_GAIN_IIR_SAA=true` while setting `HEADSTAGE_TIM=false`, `RADIO_BASIC=false`, `RADIO_AGC=false`, `RADIO_AGC_IIR=false`, and `RADIO_AGC_IIR_SAA=false`.

Then `make clean; make` to compile.

To compile gtkclient to work with other [firmware versions on RHD-headstage](#firmware-versions), set the corresponding option among `HEADSTAGE_TIM`, `RADIO_BASIC`, `RADIO_AGC`, `RADIO_AGC_IIR`, `RADIO_AGC_IIR_SAA` and `RADIO_GAIN_IIR_SAA` to `true` while setting the others to `false`.

## <a name="running-gtkclient">Running gtkclient</a>

Communication between gtkclient and the headstages work as follows:

1. When gtkclient is launched, it listens on the network for multicast messages.
2. When the bridges are launched, it sends out multicast packets.
3. gtkclient spawns `NSCALE` threads to listen for multicast packets from bridges. When a bridge packet is received, the sender bridge is mated with gtkclient, and one of these threads then handles all traffic from that bridge. 
4. gtkclient assigns the bridges to operate on the radio frequency given in the `g_radioChannel` array.
5. Each bridge then can exchange traffic with the headstage operating on the same radio frequency. The bridges then relay these traffic to gtkclient.

This protocol makes it necessary for `NSCALE` to match the number of bridges and headstages used, for different bridges to have different MAC addresses, for different headstages to operate on different radio frequencies, and for the headstage radio frequencies to match the ones in `g_radioChannel`.

Since this communication protocol requires using multicast traffic, it is necessary that if the bridges and the client PC are all connected to the same router/switch, the router/switch must be configured to disable multicast/IGMP filtering. Note that switches commonly allow multicast/IGMP traffic by default.

Also, make sure the client PC allows `allmulti` traffic for the ethernet interface by `sudo ifconfig eth0 allmulti` or adding the line to `/etc/network/interfaces` file to enable multicast permanently.

After compilation, gtkclient can be launched from the directory `myopen_multi/gtkclient_multi` by `./gtkclient`. It is recommended to turn on the the bridges after launching gtkclient to ensure mating. In the terminal window, messages such as:

```
Thread 140129180382976: rxed buf= neurobrdg
Thread 140129180382976: a wild bridge appears at 10.145.39.253
Thread 140129180382976: radio channel set to 84. It's super effective!
```
indicates 1) gtkclient has received a multicast packet `neurobrdg`, which 2) indicates the presence of a bridge at 10.145.39.253, and 3) the bridge is configured to operate on radio channel 84. `Thread 140129180382976` is the thread gtkclient spawned that is taking care of this new bridge.

There will be one series of these messages for each bridge turned on. The absence of these messages indicate a problem in multicast traffic communication. Make sure the routers are configured correctly and the computer's ethernet interface allows allmulti.

During operation, the headstages send packets containing waveform and spike matching data wirelessly to the bridge. The bridge then check and timestamps the packets to send to gtkclient. When gtkclient receives the packets from the bridge, it then processes the encapsulated data and renders display accordingly. An iterative estimate of the clock skew between the computer's performance counter and the timestamps received from the bridge is kept by gtkclient for timing.

Actions made in the gtkclient GUI may result in command packets sent from gtkclient to the bridge, then to the headstages, establishing two-way communication.

The gtkclient interfaces for both RHA-headstage and RHD-headstage are largely similar. It's recommended to read this entire section to understand the interfaces and their differences.

## <a name="RHAgtkclient">RHA-headstage gtkclient</a>

Below is a screenshot of the main interface of gtkclient compiled for RHA-headstage (`HEADSTAGE_TIM=true`), when the `rasters` tab is selected.

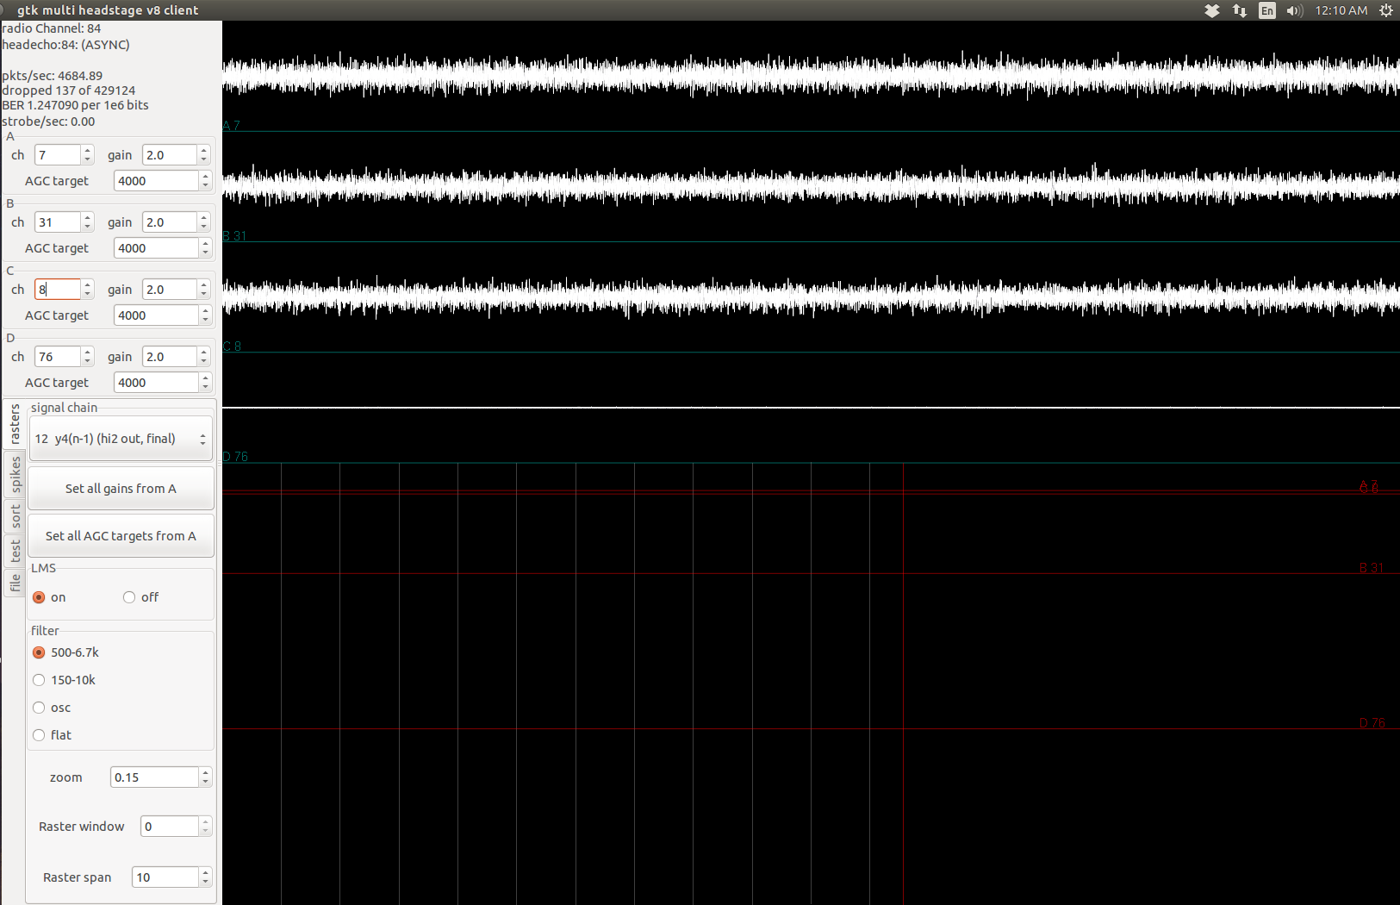
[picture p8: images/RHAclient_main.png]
RHAclient_main


On the top left corner, the message

```
radio Channel: 84
headecho:84:(SYNC)
```

displays the radio channels from `g_radioChannel`, which the bridge is configured to operate on.

Below that,

* `pkts/sec` displays the rate at which gtkclient is getting packets from the bridges, which is a good estimate of the number of wireless packets the bridge has received from the headstages.

* `dropped` shows how many packets have been lost or dropped since launching gtkclient due to wireless transmission. This number will always increase if the headstages are operating correctly. See [Debugging radio transmission] for more.

* `BER` shows the Bit Error Rate. When bit error happens with received packets, they are rejected by gtkclient.

* `strobe/sec` shows the rate at which gtkclient receives strobe packets, which is how other programs such as BMI3 request spike information from gtkclient.

Below that are four channel selection boxes, and their corresponding gain setting and AGC target setting inputs. Each group of three input boxes is labeled `A`, `B`, `C` or `D`. The signals from the selected channels are plotted correspondingly on the right. The headstages can transmit raw waveforms for only four channels at a time.

When one headstage is used, the range of channels is 0 to 127. When two are used, the range is 0 to 255, and so on.

In the waveform window, teal lines separate each plot, and purple lines represent 0 -- the signal level of seen by the reference electrode.

Below the channel selection, five tabbed panes may be selected - `rasters`, `spikes`, `sort`, `test`, and `file`. Displayed in the previous screenshot is the `raster` tab, which includes the signal-chain and raster-display configurations.

The `gain` and `AGC target` settings configure signal-chain parameters of the firmware onboard the RHA-headstage. The signal-chain consists of a series of stages that processes the samples from the ADC, all preceeding the spike template matching step.

For the RHA-headstage, the signal chain includes, in cascading order (details can be found in Tim's thesis and the links near the start of this document):

1. Automatic Gain Control (AGC) - amplifies the incoming signal so that the resulting signal has a fixed power level. The power level of each channel can be set with the `AGC target` input when that channel is selected. The button `Set all AGCtargets from A` sets the AGC target for all channels from all headstages to that of channel A.

2. Least Mean Squared (LMS) adapative noise cancellations - attenuates the noise from one channel using the signals from the previous 7 channels. This stage can be turned off for all channels by choosing the `off` option in the `LMS` box.

3. Infinite Impulse Response (IIR) digital filters. The RHA-headstage firmware implements an 8-pole butterworth bandpass filter by cascading four direct-form I biquads. The coefficients of these filters can be set in specific ways.

    * The value given to the `gain` setting results in new set of filter coefficients that are written to the headstage. The gain range is between -2 and 2.
    * The `500-6.7k` option in the `filter` box sets the filter on the four channels selected to pass the frequencies between 500Hz and 6.7kHz. This is the default option.
    * The `150-10k` option in the `filter` box sets the filter on the four channels selected to pass the frequencies between 150Hz and 10kHz. 
    * The `osc` option in the `filter` box sets the filter on the four channels such that the filter outputs oscillate at roughly 250Hz, with amplitude depending on the signal power prior to selecting this option. Note that the oscillation is only displayed when the `12 y4(n-1) (hi2 out,final)` option is selected in the `signal chain` box. 
    
        This is an easy way of checking if the wireless linke between the bridge and headstage is working. If there is a noticeable delay between checking this option and the waveforms showing oscillations, then the link quality is poor. Possible solutions include changing locations of the bridge/antenna, and restarting gtkclient and the bridges.

    * The `flat` option in the `filter` box sets the filter to pass all frequencies.

    Note that the default option for the `filter` box is `500-6.7k`. If another option e.g. `osc` is selected the changes will apply only to currently displayed channels (say Channel 7, 31, 8, and 16). When different channels are selected, the radio button for `osc` will still be selected, regardless of the new channel's filter settings.

The first selectable box on the `raster` page allows the user to select what part of the signal chain the headstage will transmit. The default option is `12 y4(n-1) (hi2 out,final)`, which is the output of the last stage of IIR filters.

The available options include:
* `0 mean from integrator`: Intermediate value used in the AGC stage, similar to an estimate of the raw input signal power.

* `1 AGC gain`: channel's AGC gain

* `2 LMS saturated sample`.

* `3 AGC out / LMS save`: Output of the AGC stage.

* `4 x1(n-1) / LMS out`: Output of the LMS stage, and input to the first IIR biquad.

* `5 x1(n-2)`: Input to the first IIR biquad from last time step.

* `6 x2(n-1) / y1(n-1) (lo1 out)`: Output of the first biquad, equivalent to the input to the second biquad. `lo1 out` indicates that the first biquad implements the first lowpass stage of the bandpass filter.

* `7 x2(n-2) / y1(n-2)`: Last time step's output of the first biquad/input to second biquad.

* `8 x3(n-1) / y2(n-1) (hi1 out)`: Output of the second biquad, equivalent to the input to the third biquad. `hi1 out` indicates that the second biquad implements the first highpass stage of the bandpass filter.

* `9 x3(n-2) / y2(n-2)`: Last time step's output of the second biquad/input to third biquad.

* `10 x4(n-1) / y3(n-1) (lo2 out)`: Output of the third biquad, equivalent to the input to the fourth biquad. `lo2 out` indicates the the third biquad implements the second lowpass stage of the bandpass filter.

* `11 x4(n-2) / y3(n-2)`: Last time step's output of the third biquad/input of the fourth biquad.

* `12 y4(n-1) (hi2 out, final)`: Output of the fourth biquad, also the output of the entire signal chain, and the default option selected. `hi2out, final` indicates the fourth biquad implements the second highpass stage of the bandpass filter.

* `13 y4(n-2)`: Last time step's output of the fourth biquad.

The ability to inspect all these intermediate values provide great debugging value.

Below the four waveform displays is the raster display, which shows detected neural spikes as blue or yellow dots. The four horizontal red lines indicate the channels whose waveforms are currently displayed. The vertical red line indicates the current time.

The `zoom` selection box sets the time length of the the displayed data for the waveform display (see `zoomSpinCB()` in `src/gtkclient.cpp`).

The `Raster Window` selection box selects which channels' rasters are viewed. Each raster window displays the rspikes for 128 channels. If only one headstage is used, this option is inactivated. If two headstages are used, a value of `1` will display the rasters for channel 128-255, corresponding to channels from the second headstage.

The `Raster span` selection box sets the time length of the displayed data for the raster display (see `g_rasterSpan` in `src/gtkclient.cpp`).

## <a name="RHDgtkclient">RHD-headstage gtkclient</a>

Below is a screenshot of the main interface of gtkclient compiled for RHD-headstage <s>deployment</s> firmware (`RADIO_AGC_LMS_IIR_SAA=true`), with the `raster` tab selected.

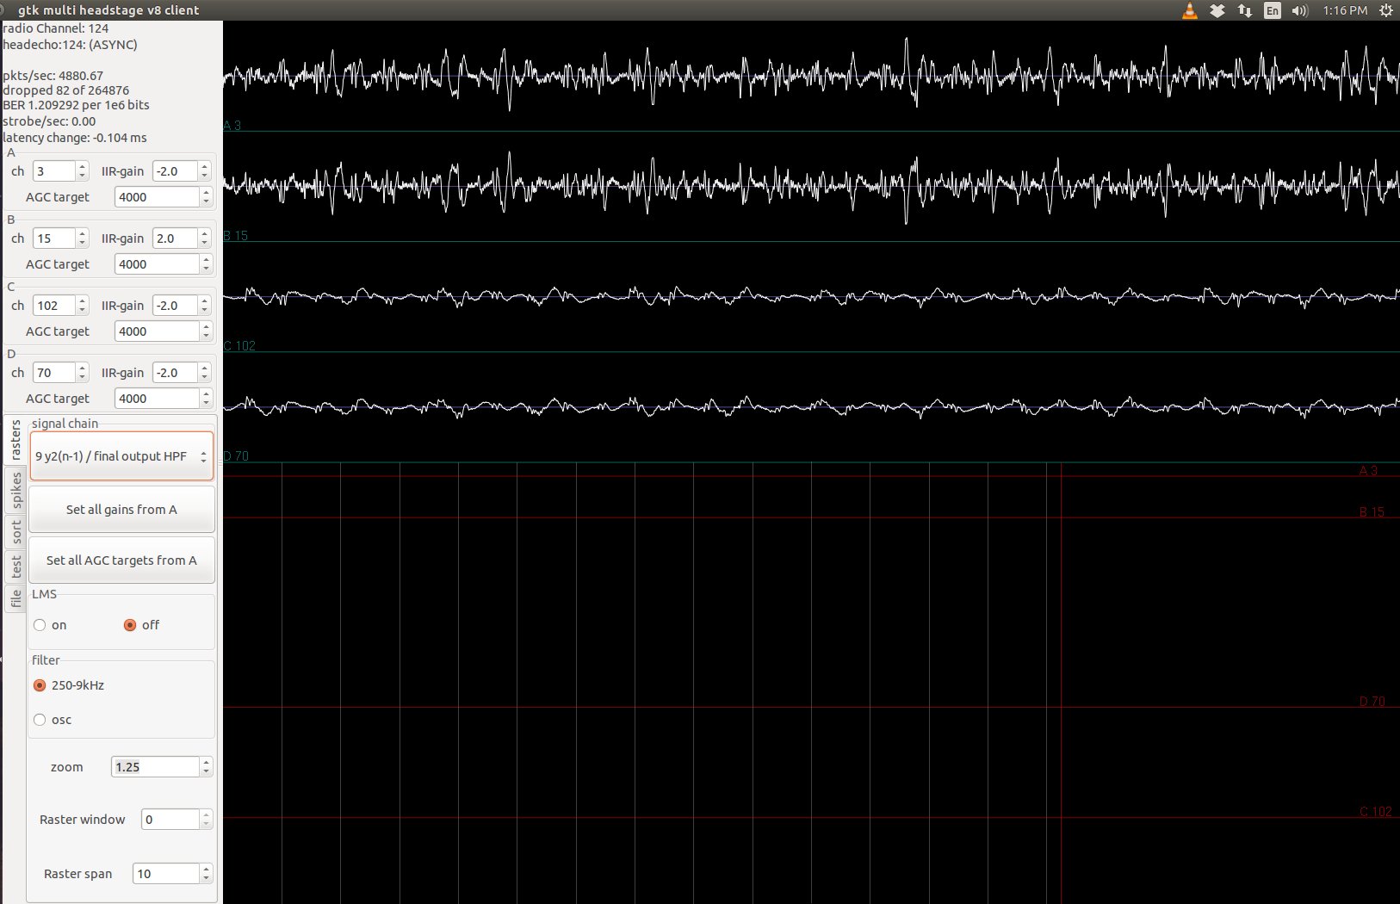
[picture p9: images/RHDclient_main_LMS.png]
RHDclient_main_LMS


It is now mostly identical to that of the RHA-headstage gtkclient. The biggest difference is the options available in the signal-chain selection box.

These differences reflect the differences in the DSP signal-chain implemented. Specifically, we have introduced `Samples from Intan` as the first inspectable signal, and the removal of the `x4(n-1)/y3(n-1)` to `y4(n-2)` items from the signal chain. The removal is due to the RHD-headstage only implement two IIR biquads instead of 4.

We have reduced the available filter options to either inducing osccilation using `osc`, or use the default option of `250-9kHz`. The `osc` option sets the filters to oscillate at 250Hz instead of 919Hz used in RHA-headstage.

The default signal chain, and that immediately preceeding spike sorting is `9 y2(n-1)/final output HPF`.

The available options are:
* `0 Samples from Intan`: They are samples output by the Intan RHD2132 amplifiers, before any DSP from the blackfin.
* `1 Integrated mean`: Intermediate value used in the AGC stage, similar to an estimate of the raw input signal power.
* `2 AGC gain`: channel's AGC gain
* `3 Saturated AGC out`: Saturated Output of the AGC stage, used for LMS stage after.
* `4 AGC/LMS out`: Ouput of the LMS stage. If LMS option is turned off, this is equivalent to AGC stage.
* `5 x1(n-1)/LMS out`: Output of the LMS stage, input to the first IIR biquad.
* `6 x1(n-2)`: Last time step's input to the first IIR biquad.
* `7 y1(n-1) LPF`: Output of the first IIR biquad, equivalent to input to the second IIR biquad.
* `8 y1(n-2) LPF`: Last time step's output of the first IIR biquad/input to the second IIR biquad.
* `9 y2(n-1)/final output HPF`: Output of the second IIR biquad, final output of the signal chain. It's the default option.
* `10 y2(n-2) HPF`: Last time step's output of the second IIR biquad.
    
## <a name="SpikeSorting">Spike sorting</a>
Below is a screenshot showing the RHDgtkclient-gain's `spikes` tab. Other than the absence of AGC setting, it is identical to RHAclient's.

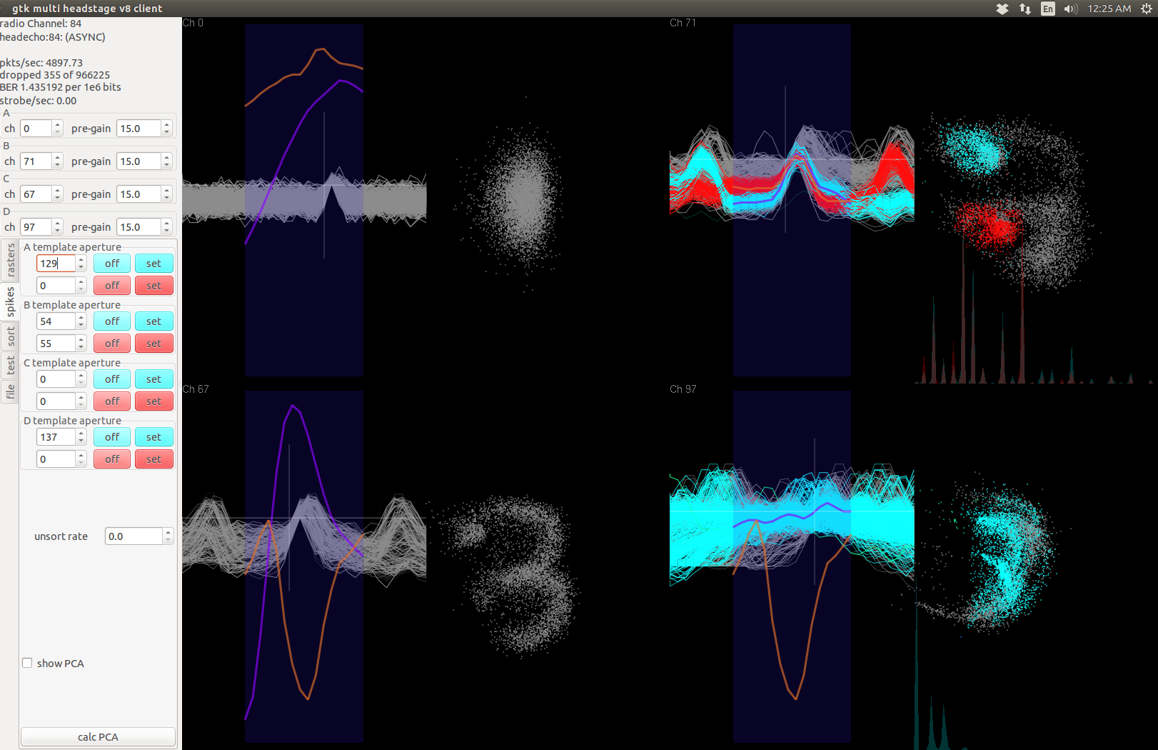
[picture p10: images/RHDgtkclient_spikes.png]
spike_page


Spike sorting in gtkclient is very similar to that used by Plexon's SortClient and OfflineSorter. Four channels can be sorted at a time, corresponding to the channels being transmitted. 

Waveforms are extracted around threshold and overlaid in each channel's window. The threshold can be set in both time and voltage domain. The threshold point is indicated by the intersecting gray lines in each channel's windows. Threshold is positive-only. The threshold values will be displayed on the left when the `sort` tab is selected.

The PCA-projection of the overlaid waveforms are shown as dots to the right of the waveforms. Holding down the right mouse-button while moving through the points will show the corresponding waveform in green. Double-clicking at the area will recalculate the PCA-projection, this is useful to reset the PCA view.

The PCA-projected points can be selected via a polygonal lasso - left-clicking and tracing out a loop. Right-clicking the selected area gives the options of `set as template 1 (cyan)` and `set as template 2 (red)`. If one of these options is selected, the mean and L1 norm of the selected points are computed, and sent to the headstage as the template and aperture for spike-matching.

The selected points, and any future points in the future that fall within the selected area will then turn cyan or red. The aperture of the set templates are also displayed on the left side of the `spikes` page. The overlaid waveforms that correspond to the colored PCA-projections will also change from gray to assume their corresponding template colors. Waveforms that don't belong to either sorted clusters will remain gray.

In the screenshot, both templates have been set for channel 71 (not really spikes, but just demonstrating the sorting tool). In all the overlaid waveform windows, there are also thicker orange and purple traces. Those are the 16-points waveform templates for those channels (as a result of calculating the mean of PCA-projections). These traces change whenever a template is set through the polygonal lasso. Note that the width of the 16-points templates are limited within the faint blue strip, which is more narrow than the overlaid waveforms.

After the template and apertures for a channel are set and sent to the headstage, they will be used to detect spike onboard the headstage. The detection of spikes are sent along with raw waveform data in the radio packets, and these spikes are plotted in the raster window. When a channel is also one of the four channels whose raw samples are streamed, gtkclient will convolve the templates for that channel with the last 24 continuously transmitted samples and compare against the corresponding aperture to check for spikes. If gtkclient detects a spike but the radio packet does not report one, then `missed spike` message will be printed out in the terminal. If gtkclient does not detect a spike, but the radio packet does, then `false positive` message will be printed out instead.

When spikes are detected, the interspike interval, binned at 768us spike sample rate is plotted on the bottom of the PCA-projection window. This can be seen in the screenshot as well for channel 71. 

## <a name="SavingRecordings">Saving recordings</a>

Below is a screenshot showing the client's `file` tab, identical for both RHAgtkclient and RHDgtkclient.

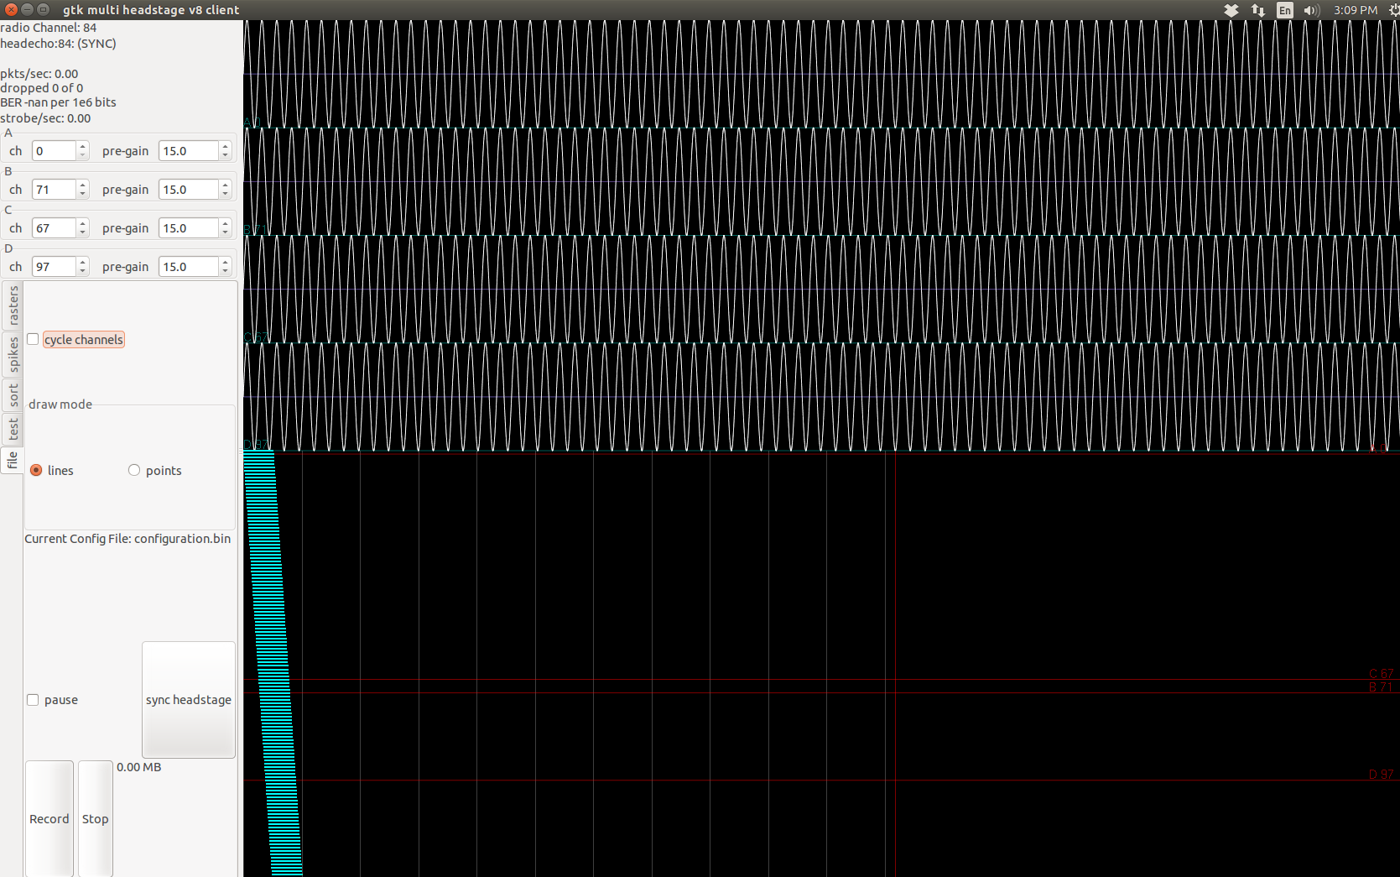
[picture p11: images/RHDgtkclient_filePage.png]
files_page


The right side of the window for the `file` tab is identical to that of `raster` tab. In the screenshot, the spikes detected on channel 31 are more visible as yellow and blue dots on the raster display.

On the left side, the `files` tab provides several configurations:

1. `cycle channels` checkbox. When checked, each of the four selected channel number will increment by 1 every 3 seconds.

2. `draw mode` box:
    * When `lines` option is selected, the raw waveforms displayed here, as well as the overlaid waveforms in the spike-sorting view will have lines connecting the received sample points. This is default option, and is the most intuitive plotting option.
    * When `points` option is selected, the raw waveforms displayed here, as well as the overlaid waveforms in the spike-sorting view will simply plot the individual sample points. The display results will be more difficult to inspect, but it is useful when the amount of rendering needed increases, as a result of rapidly varying waveforms with high amplitudes and/or a lot of spike detections to plot.

3. The text `configuration.bin` is displayed below the `draw mode` box. This indicates the configuration file we are reading from/writing to. See [Configuration files section](#gtkclientConfigurations).

4. The `sync headstage` button, when pressed, will reset the signal-chain and spike-matching parameters stored on the headstage to match those set in gtkclient. A noteable exception is that the IIR filters will be reset to 500Hz to 6.7kHz bandpass for RHAgtkclient, and 500Hz to 9kHz bandpass for RHDgtkclient, regardless of what option is set in the `filters` box, which will not change.

5. The `record` button initiates the recording process. When pressed, file dialog will prompt for where to save the file.

6. The `stop` button stops the recording to file. The size of the recording is shown under the `sync headstage` button.

7. The `pause` checkbox pauses an ongoing recording.

The recording files are saved as a binary file. The data recorded include:

* Received incoming packets in addition to client clock and bridge clock.
* Outgoing packets, along with ASCII versions of the commands.

The program `convert` is compiled along with gtkclient from `src/convert.cpp`. Running `convert infile.bin` yields four output files from the saved recordings, which can be easily processed in Matlab.

* $.mat, which contains the vectors:
    * `time` - wall time within the client, synchronous to the BMI (or any program requesting firing rates through TCP/IP).
    * `mstimer` - hardware clock on bridge, runs at 9155.273438Hz. One entry per received packet. Timestamps for spikes should be pretty accurate.
    * `spike_ts` - spike times, indexes time and mstimer. The spikes are matched on the headstages but only timestamped on teh bridge to conserve bandwidth. Note that `spike_ts` indexes into `time` and `mstimer` in C-style, which is 0-indexed. When using in MATLAB, add 1 to this vector.
    * `spike_ch` - Channel of the spikes detected, same length as `spike_ts`.
    * `spike_unit` - Unit of the spike detected in a channel. Same length as `spike_ts`. Note this wireless system assumes that both units in a channel can't fire at once.
    * `radio_ch` - Radio channel of each received packet.
    * `t_id` - Sock-thread id (each sock thread handles communication with each bridge) of each received packet.

* $.nlg: Contains raw signed 8-bit integer matrix of analog traces (the continuously transmitted four selected channels). It's a matrix of 4x(received packets x 6). Each packet contains 6 samples from 4 channels. The script `plot_raw_channels.m` will plot these signals given the name of the nlg file.

* $.chn.gz: gzipped version of the channel information of the raw analog traces.

* $.log.gz: gzipped text of messages within the file (i.e. ASCII versions of the outgoing commands)

To plot the analog traces, see [plot_raw_channels.m](https://github.com/allenyin/recording_validation/blob/master/analysis/plot_raw_channels.m).

To convert the spike times relative to recording start, the following scheme can be used:

```matlab
load(spikeFile);                % load .mat file
f_mstimer = 9155.273438;        % hardware clock in Hz
mstimer = double(mstimer);      % convert from uint32 to double
spike_ts = spike_ts+1;          % convert to 1-indexed

mstimer = mstimer - mstimer(1); % process mstimer to start at 0
mstimer = mstimer/f_mstimer;    % convert values in mstimer to seconds
spikeTimes = mstimer(spike_ts); % spike times in bridge time, in seconds
```

## <a name="TestRecording">Test recording</a>

Below is a screenshot showing the client's `test` tab, identical for both RHAgtkclient and all versions of RHDgtkclient.

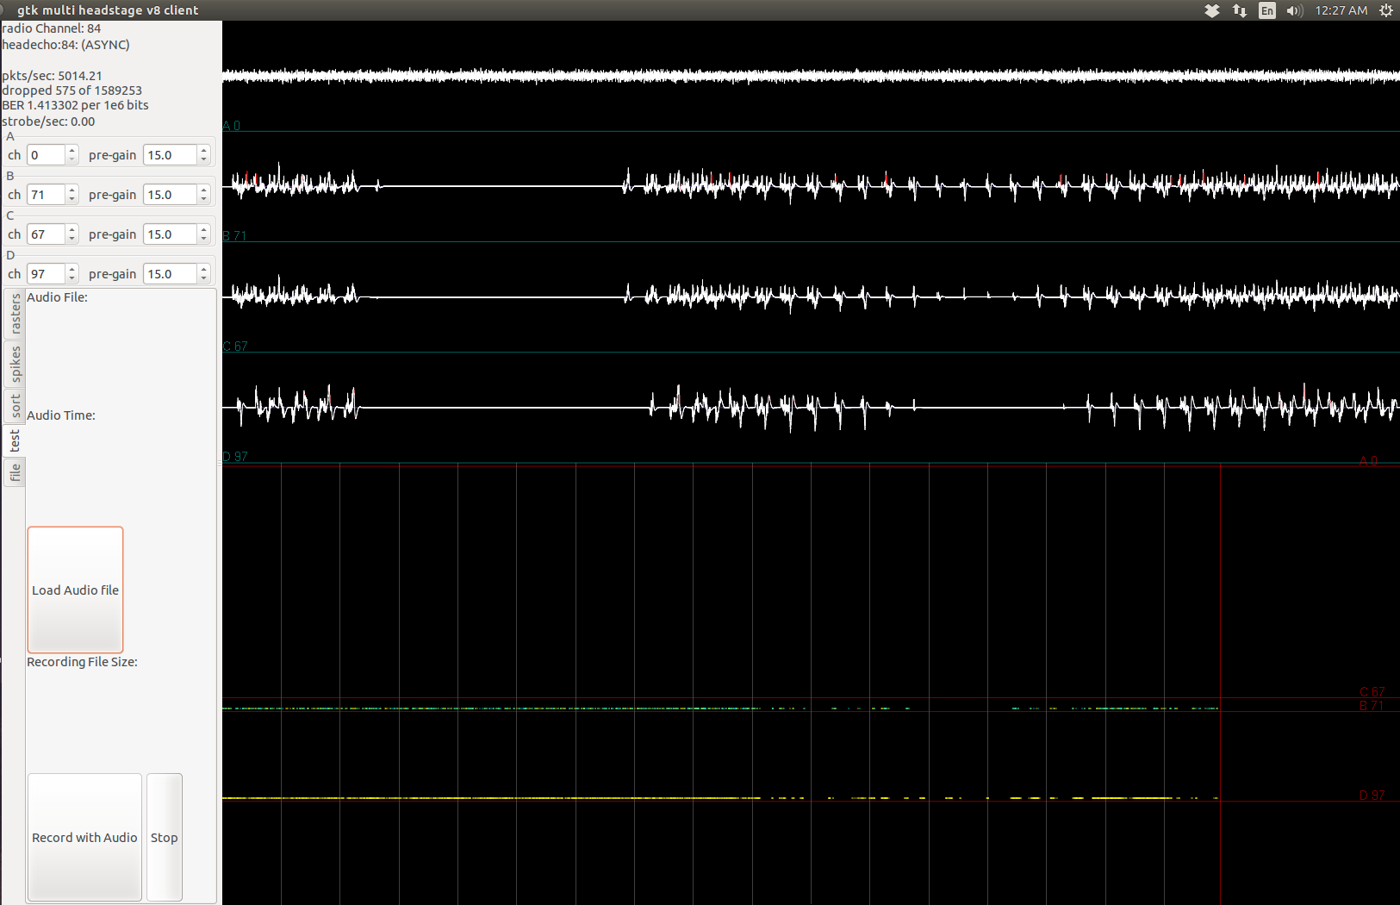
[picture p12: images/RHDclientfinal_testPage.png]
test_page


The right side of the window for the `test` tab is identical to that of `raster` tab. In the screenshot, the spikes detected on channle 71 are more visible as yellow and blue dots on the raster display.

On the left side, the `test` tab provides several buttons. The purpose of this tab is to facilitate [recording from simulated signals](http://allenyin.github.io/reading_list/2016/03/WirelessValidationPktLoss). Simulated signals can be saved as audio files and played from the same computer where gtkclient runs. The audio signal can be passed to the wireless headstages (RHA or RHD) via [Plexon headstage tester units](http://www.plexon.com/products/headstage-tester-units). This page allows the user to specifiy the audio file, and start both the recording and audio with minimal delay.

1. `Load Audio File`: Brings up a dialog asking the user to specify the desired audio file. After selection the file's name will be displayed under the `Audio File:` field.

2. `Record with Audio`: Brings up a dialog asking the user where to save the recording file. After selection, the recording will be started, along with vlc playing the selected audio file. There is roughly a 0.4-0.5 seconds delay between recording start and vlc playback start. The recording file size as well as audio time (min:sec) will be displayed. While a recording initialized this way is happening, pressing the `record` button in the `file` page triggers nothing, and vice versa.

3. `Stop`: Stops the recording. Allows new recording to be initiated subsequently from either `test` or `file` page.

## <a name="gtkclientConfigurations">Configuration files</a>

Instances of gtkclient saves information about its state via [protobuf](https://developers.google.com/protocol-buffers/docs/cpptutorial) in two binary files: `state.bin` and `configuration.bin`.

Upon launching, gtkclient looks for these two files. Sorted spike templates, channel threshold, signal chain settings and radio channel information settings are all saved in `configuration.bin`. If these files do not exist when gtkclient is launched, they will be created.

It's important to remember that the session's settings will only be saved at the end if gtkclient is terminated by clicking the 'x' button on the GUI. Forced termination using `ctrl-c` will result in losing these setting information.

If you want to use the sorted templates created from a different gtkclient instance (from another computer or in a different folder), simply copy the `configuration.bin` from that instance to the current gtkclient directory. Upon launching, the copied over `configuration.bin` file will be read instead. You might want to back up the replaced file for later.

**Caution**
However, be careful to not mix the usage of RHA-headstage/gtkclient generated templates with that generated by RHD-headstage/gtkclient. This is because not only the headstages differ in electrode layout (e.g. channel 31 on RHA-headstage is actually channel 23 on RHD-headstage), but also since the DSP signal-chains differ, the user would have to go through all the channels to resort.

In general, do not mix using RHA-headstages with RHD-headstages.

## <a name="TCPgtkclient">Communication with other programs</a>

gtkclient can send firing rates information to requester throgh a TCP/IP socket. See Skunkape for implementation.

## <a name="gtkclient-TODO">TODO/possible improvements</a>
* More threadsafe

* Redsicovery of bridges after gtkclient is killed...maybe implement by remembering IP of bridges?

* Spatial bridge redundancy to improve range? Need to rewrite the multicast protocol to bind then..

* Graphics improvements --opengl??

* UI improvements. For example, doing `sync headstage` result in resetting the radio buttons in `filters` box..will require exposing the buttons pointer.

---------------------
This section has only covered using gtkclient compiled with `HEADSTAGE_TIM` option (for RHA-headstage), and that compiled with `RADIO_AGC_IIR_SAA` option (for RHD-headstage). 

Compilations of gtkclient with the other RHD-headstage options contains a subset of the `RADIO_AGC_IIR_SAA` gtkclient's functions.

## <a name="quickstart">Quick Start</a>

Here are steps to use 2 RHD-headstages with deployment firmware:

1. Follow the [bridge flashing instructions](#Bridge-hw) to flash two bridges, making sure they have different MAC addresses. It is ok to skip this step if there are two existing bridges known to be flashed already and have different MAC addresses.

2. Follow the [RHD-headstage flashing instructions](#RHD-fw) to flash two RHD-headstages, making sure they have different radio channels. Modify gtkclient as instructed and recompile. When connected to battery, the LED should blink.

3. Launch gtkclient inside the `myopen_multi/gtkclient_multi` with `./gtkclient`.

4. Turn on the bridges. The terminal from which gtkclient is launched should print out two sets of messages such as

    ```
    Thread 140129180382976: rxed buf= neurobrdg
    Thread 140129180382976: a wild bridge appears at 10.145.39.253
    Thread 140129180382976: radio channel set to 84. It's super effective!
    ```
    indicating the bridges have been discovered by gtkclient.

5. Waveforms should start appearing on the waveform plots when gtkclient's `raster` or `files` tab is selected. If not, check if the heastages are powered, and if the radio-channels were set up correctly.

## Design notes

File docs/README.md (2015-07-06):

#allen_wireless

Modified from the wireless neural recording parts of the [myopen project](https://github.com/tlh24/myopen) by Tim Hanson.

Folders:

* bridge_hardware: port from [stage10](https://github.com/tlh24/myopen/tree/master/emg_dsp/stage10). Components  stored in bridge_library/. Footprint archived to bridge_library.pretty/ to use with newer version of kicad (Version:0.201506030104+5696~23~ubuntu14.04.1-product,release build).
* headstage_hardware: port from [stage9](https://github.com/tlh24/myopen/tree/master/emg_dsp/stage9). Components stored in headstage_library/. Footprint archived to headstage_library.pretty/ to use with newer version of kicad.
* headstage2_hardware: based on stage9. Uses 4xRHD2132 amplifiers rather than 4xRHA2132 amplifiers front-end. Eliminated separate ADCs and analog power-supply components.
* myopen_multi: Modified from [myopen's multi branch](https://github.com/tlh24/myopen/tree/multi). Includes:
    * bridge_firmware: previously [firmware_stage7](https://github.com/tlh24/myopen/tree/mutli/firmware_stage7).
    * headstage_firmware: previously [firmware_stage9_tmpl](https://github.com/tlh24/myopen/tree/multi/firmware_stage9_tmpl). Uses templates matching to transmit spike timings from the headstage.
    * gtkclient_multi: The wireless gtkclient. Makefile modified to compile on Ubuntu. Need to recompile for newer protobuf versions.
    * flasher: Code used to write to the flash memories of the bridge and headstage, see Instructions in crispy.
    * common_bfin: Common blackfin files.
    * common_host: Files for bridge.
    
    TODO: Sync the firmware with the ones in Rabbit, which are actually used to flash the hardware. Sync the gtkclient_multi with that in the wheelchair room, and write up instructions of limiting the number of threads to be the same as the number of headstages/bridges been used.

---
##Steps to port old kicad projects

The recent changes in KiCad's EESchema introduces some problems in using projects created with older version out of the box. Those impacting include:

0. Updated device library. The new device library footprints are smaller, this can cause older schematics to be displayed with broken connections. Solution: follow the procedures outlined [here](https://lists.launchpad.net/kicad-developers/msg17639.html) to use the rescue-lib.
0. Saving the old .brd files will convert them to .kicad_pcb. Subsequent openning of the board files will then result in parse errors and no board. Solution: Never save!!! (have not yet found a good solution).

In general, the KiCad files in bridge_hardware and headstage_hardware are for reference only, no save/modification should be needed.

The following steps were used to convert the old project files (example using headstage_hardware/):

0. Extract stage9 from /emg_dsp.
0. Create component and footprint library folders. `cd headstage_hardware; mkdir headstage_library headstage_library.pretty`
0. Open the schematic file, press OK for the rescue components dialog. Copy the cached component to our newly created library: `cp stage9-cache.lib headstage_library/headstage.lib`
0. Go to *Preferences*->*Component Libraries* and add headstage as an active library.
0. Ctrl-E on any of the component to open library editor. Set active library to be *headstage* and save component.
0. Close schematic and open again. Now editing any of the components in the library editor should show the active library as *headstage.lib*
0.  **Important! When closing the schematic, do not click on save!**
0. Open the .brd file, click ok on the resulting dialog.
0. Ctrl-E on any of the footprint to open the footprint editor. Click on *Create new library and save footprint* from the menu bar, and select the *headstage_library.pretty* folder to store the new library.
0. Go to *Preferences*->*Footprint libraries Wizard*->*Files on my computer* and select the *headstage_library.pretty* folder. This will add that directory to the footpring libraries available in this project. Make sure to select avaliable to project only.
0. *Select active library* in the footprint editor and make it *headstage_library.pretty*.
0. Close footprint editor and go back to the board. Go to *file*->*Archive Footprints*->*Create footprint archive* and select *headstage_library.pretty* as the library. Click yes to replace library. Now *headstage_library.pretty/* contains all the footprint used in the board as .mod files.
0. Make sure when footprint editor is opened, the active library is set correctly to the one we just created.
0. Again remeber to **Not save the board file!!**
0. Open the schematic file and run Cvpcb to associate the components and the footprints in our own custom libraries. It's possible that a footprint is found in multiple libraries, chose to associate with the ones in *headstage*.

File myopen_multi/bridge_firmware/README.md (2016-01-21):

#Firmware for wireless headstage bridge

The bridge units are the same, regardless of the headstages used -- either the older, RHA-based headstages (Tim Hanson's myopen project), or my RHD-based headstages.

**Flashing Instructions**

1. Using flashing cable (red in picture below) plugged into the computer's parallel port, plug into the bridge's SPI port as illustrated.
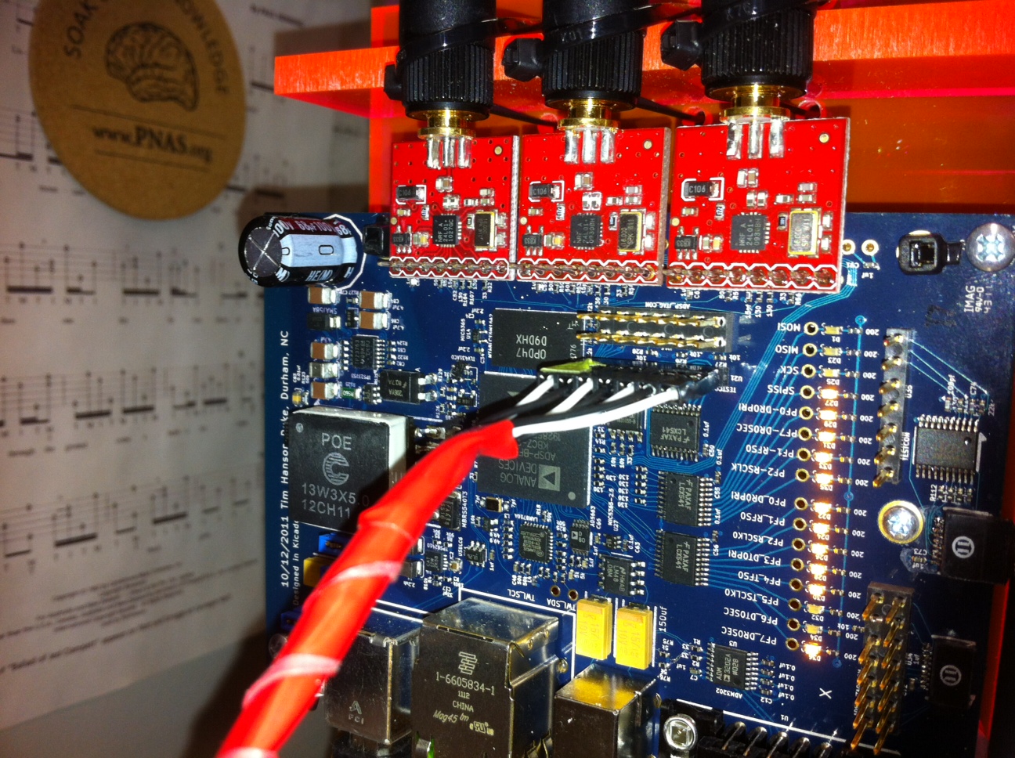
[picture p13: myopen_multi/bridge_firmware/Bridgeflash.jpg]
bridge connection


2. If using multiple bridges at the same time, make sure the MAC addresses for the bridges are different. Go to `../common_bfin/ethernet.c`, in function `SetupMacAddr()`, change the value of `MACaddr[5]`.

3. Turn the bridge on (make sure the USB power cable is connected).

4. `make clean; make; make flash`
	If error occurs, try `sudo rmmod lp; sudo modprobe ppdev` to allow pyparallel access to the paralle port.

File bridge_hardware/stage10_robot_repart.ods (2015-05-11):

1 | 410 | P200JCT-ND (http://search.digikey.com/scripts/DkSearch/dksus.dll?Detail&itemSeq=111920214&uq=634672470394771172) | RES 200 OHM 1/10W 5% 0402 SMD | 0 | 0.00976 | $4.00
2 | 210 | 490-3890-1-ND (http://search.digikey.com/scripts/DkSearch/dksus.dll?Detail&itemSeq=111920217&uq=634672470394771172) | CAP CER 1UF 10V 10% X5R 0402 | 0 | 0.0246 | $5.17
3 | 200 | P130JCT-ND (http://search.digikey.com/scripts/DkSearch/dksus.dll?Detail&itemSeq=111920219&uq=634672470394771172) | RES 130 OHM 1/10W 5% 0402 SMD | 0 | 0.0131 | $2.62
4 | 150 | P49.9KLCT-ND (http://search.digikey.com/scripts/DkSearch/dksus.dll?Detail&itemSeq=111920220&uq=634672470394771172) | RES 49.9K OHM 1/10W 1% 0402 SMD | 0 | 0.0184 | $2.76
5 | 140 | P22KJCT-ND (http://search.digikey.com/scripts/DkSearch/dksus.dll?Detail&itemSeq=111920221&uq=634672470394771172) | RES 22K OHM 1/10W 5% 0402 SMD | 0 | 0.0131 | $1.83
6 | 100 | P10KJCT-ND (http://search.digikey.com/scripts/DkSearch/dksus.dll?Detail&itemSeq=111920223&uq=634672470394771172) | RES 10K OHM 1/10W 5% 0402 SMD | 0 | 0.0131 | $1.31
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

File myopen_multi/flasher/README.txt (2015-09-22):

flash.c:

    You need to have libparapin installed to make this work. 
    http://parapin.sourceforge.net/
    connections for making a cable: see flash.c
    note: need a 33pf capacitor between clock signal and ground 
    close to flash ram for proper timing. 

    Makefile is used to compile this program. To program the flash memory onboard either the
    headstage or bridge, in their respective firmware directory do:

    For bridges:

    1) "make clean"
    If using multiple bridges, make sure the mac addresses are different in: ethernet.c, SetupMacAddr(), need to increment index[5] (hex format).
    2) Turn bridge on
    3) "make flash"

    For headstages:

    1) "make clean"
    2) "make flash"
    In order to change the radio unit channel, search for radio_init() in the firmware file, main.c
    Also need to update the client, "gtkclient.cpp" to the channel set in the radio unit (g_RadioChannel). Less than 104 interferes with WiFi.

flash.py:
    
    libparapin doesn't seem to be working for Ubuntu-14.04. The last versio of the library was written for kernel-version 2.6.
    This version interfaces with the parallel port using the PyParallel library:
        http://pyserial.sourceforge.net/pyparallel.html
    Good examples of using this library can be found at:
        http://www.bristolwatch.com/pport/pportbits.htm
    
    The python script is a port of flash.c with minimal changes. Only tested for SST25 flash, however. 
    Makefiles in the firmware directories are changed so "make flash" calls the python script instead.

    The flashing procedures stay the same.

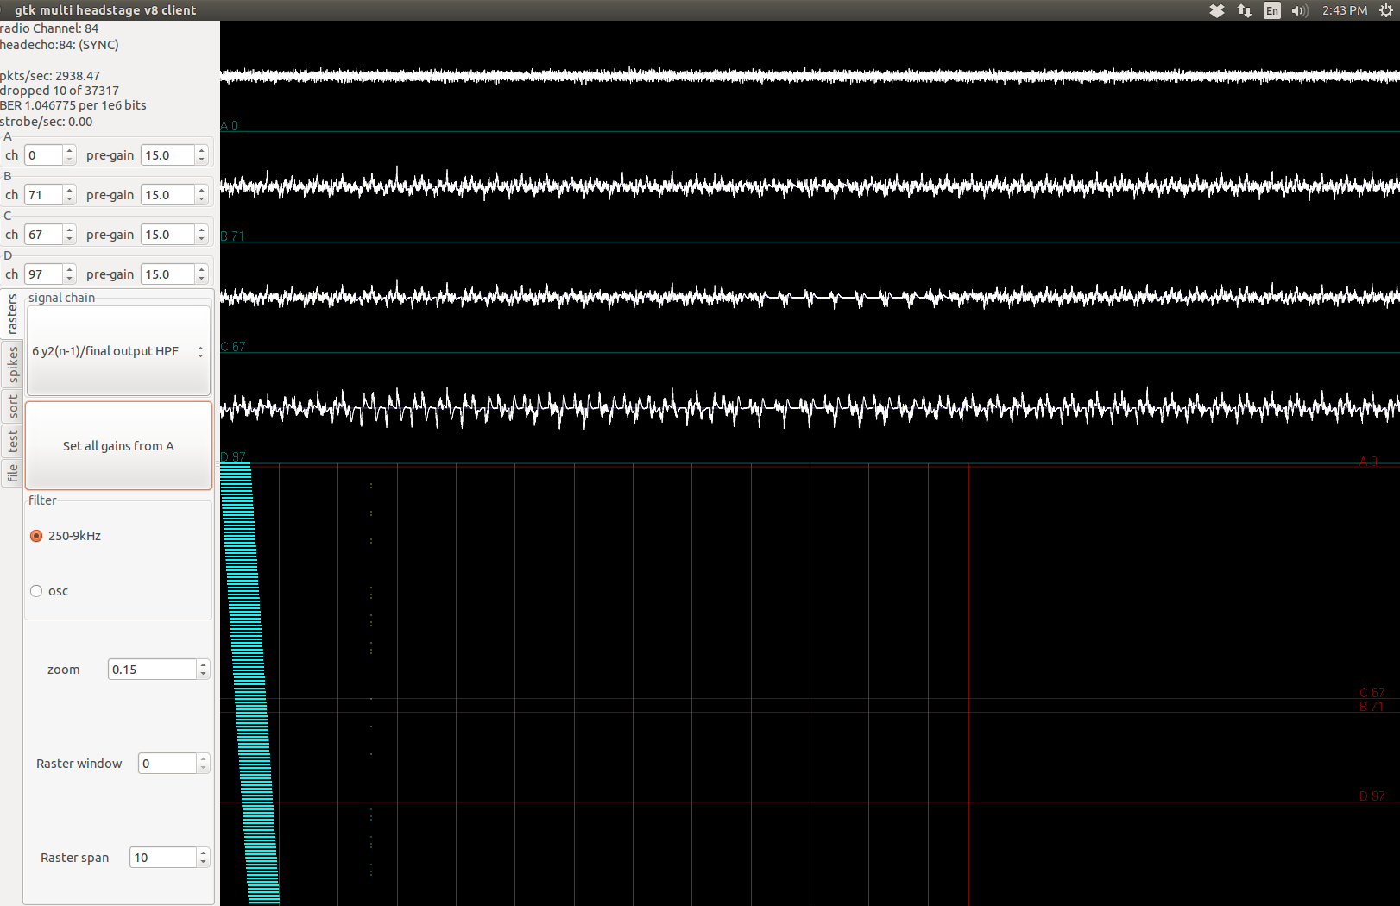
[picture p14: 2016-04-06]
images/RHDgtkclientMain_gain.png

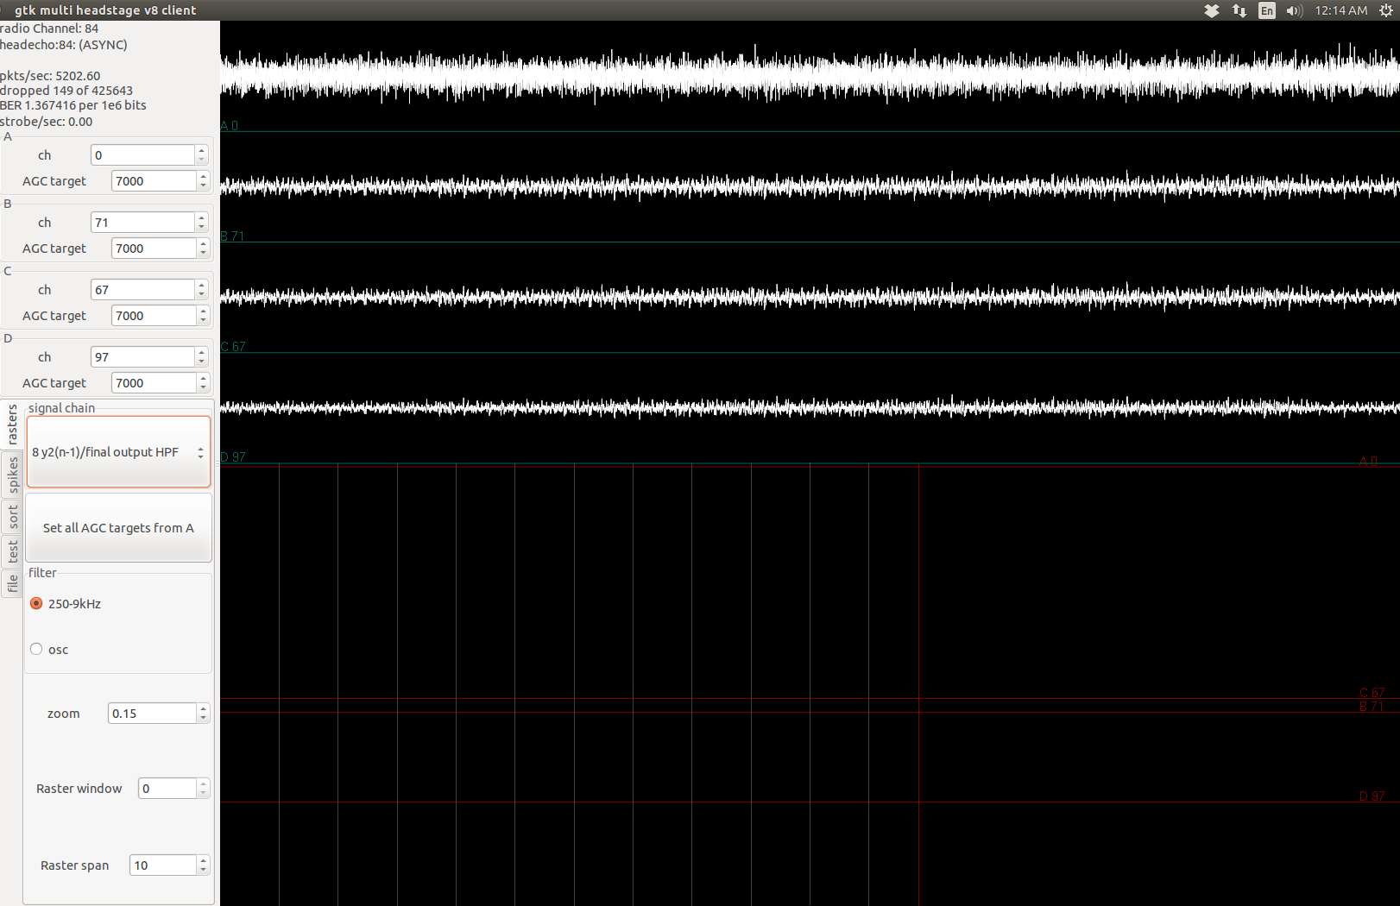
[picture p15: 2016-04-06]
images/RHDgtkclientMain_AGC.png

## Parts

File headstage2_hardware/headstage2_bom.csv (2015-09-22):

ITEM | REFERENCES | VALUE | FOOTPRINT | MANUFACTUER | SUPPLIER | SUPPLIER | PART | NUMBER | Notes
1 | C1 | 10nF | 402 | TDK | Mouser | 810-C0402X5R0J103K | ceramic, X5R, 6V
2 | C2 | 10nF | 402 | TDK | Mouser | 810-C0402X5R0J103K | ceramic, X5R, 6V
3 | C3 | 100nF | 402 | TDK | Mouser | 810-C1005X5R1C104K | ceramic, X5R, 16V
4 | C4 | 100nF | 402 | TDK | Mouser | 810-C1005X5R1C104K | ceramic, X5R, 16V
5 | C5 | 100nF | 402 | TDK | Mouser | 810-C1005X5R1C104K | ceramic, X5R, 16V
6 | C6 | 100nF | 402 | TDK | Mouser | 810-C1005X5R1C104K | ceramic, X5R, 16V
7 | C7 | 10nF | 402 | TDK | Mouser | 810-C0402X5R0J103K | ceramic, X5R, 6V
8 | C8 | 10nF | 402 | TDK | Mouser | 810-C0402X5R0J103K | ceramic, X5R, 6V
9 | C9 | 100nF | 402 | TDK | Mouser | 810-C1005X5R1C104K | ceramic, X5R, 16V
10 | C10 | 100nF | 402 | TDK | Mouser | 810-C1005X5R1C104K | ceramic, X5R, 16V
11 | C11 | 100nF | 402 | TDK | Mouser | 810-C1005X5R1C104K | ceramic, X5R, 16V
12 | C12 | 100nF | 402 | TDK | Mouser | 810-C1005X5R1C104K | ceramic, X5R, 16V
13 | C13 | 10uF | 603 | TDK | Mouser | 810-C1608X5R1E106M | ceramic, X5R, 25V
14 | C14 | 0.1uF | 402 | Murata | Mouser | 81-GRM155R71C104KA88 | ceramic,X5R,10V
15 | C15 | 10uF | 603 | TDK | Mouser | 810-C1608X5R1E106M | ceramic, X5R, 25V
16 | C16 | 7pF | 402 | Murata | Mouser | 81-GJM1555C1H7R0BB1D | crystal load: high Q, low loss, +/-0.1pF
17 | C17 | 4.7pF | 402 | AVX | Mouser | 581-04025U4R7BAT2A | crystal load: high Q, low loss, +/-0.1pF
18 | C18 | 33pF | 402 | Johansson | Mouser | 609-500R07S330JV4T | ceramic
19 | C19 | 10uF | 603 | TDK | Mouser | 810-C1608X5R1E106M | ceramic, X5R, 25V
20 | C20 | 10uF | 603 | TDK | Mouser | 810-C1608X5R1E106M | ceramic, X5R, 25V
21 | C21 | 47nF | 402 | Vishay | Mouser | 77-VJ0402Y473JXQCBC | ceramic
22 | C22 | 10uF | 603 | TDK | Mouser | 810-C1608X5R1E106M | ceramic, X5R, 25V
23 | C23 | 10uF | 603 | TDK | Mouser | 810-C1608X5R1E106M | ceramic, X5R, 25V
24 | C24 | 1nF | 402 | Kermet | Mouser | 80-C0402C102J4R | ceramic, X7R, 16V
25 | C25 | 0.1uF | 402 | Murata | Mouser | 81-GRM155R71C104KA88 | ceramic, X7R, 16V, 10%
26 | C26 | 1nF | 402 | Kermet | Mouser | 80-C0402C102J4R | ceramic, X7R, 16V
27 | C27 | 1uF | 402 | Murata | Mouser | 81-GRM155R61E105KA2D | ceramic, X5R, 25V, 10%
28 | C28 | 0.1uF | 402 | Murata | Mouser | 81-GRM155R71C104KA88 | ceramic, X7R, 16V, 10%
29 | C29 | 1nF | 402 | Kermet | Mouser | 80-C0402C102J4R | ceramic, X7R, 16V
30 | C30 | 0.1uF | 402 | Murata | Mouser | 81-GRM155R71C104KA88 | ceramic, X7R, 16V, 10%
31 | C31 | 10nF | 402 | Murata | Mouser | 81-GRM36X103K25 | cermaic, X7R, 25V, 10%
32 | C32 | 0,1uF | 402 | Murata | Mouser | 81-GRM155R71C104KA88 | ceramic, X7R, 16V, 10%
33 | C33 | 4.7pF | 402 | AVX | Mouser | 581-04025U4R7BAT2A | crystal load: high Q, low loss, +/-0.1pF
34 | C34 | 0.1uF | 402 | Murata | Mouser | 81-GRM155R71C104KA88 | ceramic, X7R, 16V, 10%
35 | C35 | 0.1uF | 402 | Murata | Mouser | 81-GRM155R71C104KA88 | ceramic, X7R, 16V, 10%
36 | C36 | 0.1uF | 402 | Murata | Mouser | 81-GRM155R71C104KA88 | ceramic, X7R, 16V, 10%
37 | C37 | 1uF | 402 | Murata | Mouser | 81-GRM155R61E105KA2D | ceramic, X5R, 25V, 10%
38 | C38 | 2.2nF | 402 | AVX | Mouser | 581-04025C222JAT2A | ceramic, X7R, 50V, 5%
39 | C39 | 1.5pF | 402 | AVX | Mouser | 581-04025U1R5BAT2A | ceramic, C0G, 50V, +/-0.1pF, RF
40 | C40 | 0.1uF | 402 | Murata | Mouser | 81-GRM155R71C104KA88 | ceramic, X7R, 16V, 10%
41 | C41 | 0.1uF | 402 | Murata | Mouser | 81-GRM155R71C104KA88 | ceramic, X7R, 16V, 10%
42 | C42 | 10nF | 402 | Murata | Mouser | 81-GRM36X103K25 | cermaic, X7R, 25V, 10%
43 | C43 | 1pF | 402 | AVX | Mouser | 581-04025U1R0BAT2A | ceramic, C0G, 50V, +/-0.1pF, RF
44 | C44 | 0.1uF | 402 | Murata | Mouser | 81-GRM155R71C104KA88 | ceramic, X7R, 16V, 10%
45 | C45 | 0.1uF | 402 | Murata | Mouser | 81-GRM155R71C104KA88 | ceramic, X7R, 16V, 10%
46 | D1 | LED | D0603? | Lumex | Mouser | 696-SML-LX0603IW | Red, 2V, 20mA, 160 view angle
47 | L1 | 2.2uH | 1210 | Taiyo | Yuden | Digikey | 587-2165-1-ND | 1.6A rating, 150MHz resonant freq, 78 mOhm DC
48 | L2 | 2.2uF | 1210 | Taiyo | Yuden | Digikey | 587-2165-1-ND | 1.6A rating, 150MHz resonant freq, 78 mOhm DC
49 | L3 | 8.2nH | 402 | Wurth | Digikey | 732-1719-1-ND | 680mA rating, 4.4GHz resonant freq, +/-5%, 100 mOhm DC
50 | L4 | 3.9nH | 402 | Wurth | Digikey | 732-1711-1-ND | 840mA rating, 5.8GHz resonant freq, +/-5%, 64 mOhm DC
51 | L5 | 2.7nH | 402 | Panasonic | Digikey | PCD1851CT-ND | 400mA rating, 5.5GHz resonant freq, +/-5%, 100 mOhm DC
52 | L6 | Ferrite | 402 | Murata | Digikey | 490-1006-1-ND | 300mA rating, 600 Ohm @ 100MHz, 600 mOhm DC
53 | R1 | 0 | 201 | Panasonic | Digikey | P0.0AGCT-ND | 0.05W
54 | R2 | 0 | 201 | Panasonic | Digikey | P0.0AGCT-ND | 0.05W
55 | R3 | 0 | 201 | Panasonic | Digikey | P0.0AGCT-ND | 0.05W
56 | R4 | 0 | 201 | Panasonic | Digikey | P0.0AGCT-ND | 0.05W
57 | R5 | 0 | 201 | Panasonic | Digikey | P0.0AGCT-ND | 0.05W
58 | R6 | 0 | 201 | Panasonic | Digikey | P0.0AGCT-ND | 0.05W
59 | R7 | 0 | 201 | Panasonic | Digikey | P0.0AGCT-ND | 0.05W
60 | R8 | 0 | 201 | Panasonic | Digikey | P0.0AGCT-ND | 0.05W
61 | R9 | 0 | 201 | Panasonic | Digikey | P0.0AGCT-ND | 0.05W
62 | R10 | 0 | 201 | Panasonic | Digikey | P0.0AGCT-ND | 0.05W
63 | R11 | 0 | 201 | Panasonic | Digikey | P0.0AGCT-ND | 0.05W
64 | R12 | 0 | 201 | Panasonic | Digikey | P0.0AGCT-ND | 0.05W
65 | R13 | 0 | 201 | Panasonic | Digikey | P0.0AGCT-ND | 0.05W
66 | R14 | 0 | 201 | Panasonic | Digikey | P0.0AGCT-ND | 0.05W
67 | R15 | 0 | 201 | Panasonic | Digikey | P0.0AGCT-ND | 0.05W
68 | R16 | 0 | 201 | Panasonic | Digikey | P0.0AGCT-ND | 0.05W
69 | R17 | 22K | 402 | Panasonic | Digikey | P22.0KLCT-ND | Thick film, +/-1%, 0.1W
70 | R18 | 22K | 402 | Panasonic | Digikey | P22.0KLCT-ND | Thick film, +/-1%, 0.1W
71 | R19 | 200K | 402 | Panasonic | Digikey | P200KJCT-ND | Thick film, +/-1%, 0.1W
72 | R20 | 909K | 402 | Panasonic | Digikey | P909KLCT-ND | Thick film, +/-1%, 0.1W
73 | R21 | 165K | 402 | Panasonic | Digikey | P165KLCT-ND | Thick film, +/-1%, 0.1W
74 | R22 | 270K | 402 | Panasonic | Digikey | P270KLCT-ND | Thick film, +/-1%, 0.1W
75 | R23 | 22K | 402 | Panasonic | Digikey | P22.0KLCT-ND | Thick film, +/-1%, 0.1W
76 | R24 | 22K | 402 | Panasonic | Digikey | P22.0KLCT-ND | Thick film, +/-1%, 0.1W
77 | R25 | 22K | 402 | Panasonic | Digikey | P22.0KLCT-ND | Thick film, +/-1%, 0.1W
78 | R26 | 22K | 402 | Panasonic | Digikey | P22.0KLCT-ND | Thick film, +/-1%, 0.1W
79 | R27 | 22K | 402 | Panasonic | Digikey | P22.0KLCT-ND | Thick film, +/-1%, 0.1W
80 | R28 | 22K | 402 | Panasonic | Digikey | P22.0KLCT-ND | Thick film, +/-1%, 0.1W
81 | R29 | 200K | 402 | Panasonic | Digikey | P200KLCT-ND | Thick film, +/-1%, 0.1W
82 | R30 | 200 | 402 | Panasonic | Digikey | P200JCT-ND | Thick film, +/-5%, 0.1W
83 | R31 | 22K | 402 | Panasonic | Digikey | P22.0KLCT-ND | Thick film, +/-1%, 0.1W
84 | R32 | 0 | 402 | Panasonic | Digikey | P0.0JTR-ND | 0.1W
85 | R33 | 0 | 402 | Panasonic | Digikey | P0.0JTR-ND | 0.1W
86 | R34 | 0 | 402 | Panasonic | Digikey | P0.0JTR-ND | 0.1W
87 | R35 | 0 | 402 | Panasonic | Digikey | P0.0JTR-ND | 0.1W
88 | R36 | 0 | 402 | Panasonic | Digikey | P0.0JTR-ND | 0.1W
89 | R37 | 0 | 402 | Panasonic | Digikey | P0.0JTR-ND | 0.1W
90 | R38 | 0 | 402 | Panasonic | Digikey | P0.0JTR-ND | 0.1W
91 | R39 | 0 | 402 | Panasonic | Digikey | P0.0JTR-ND | 0.1W
92 | R40 | 0 | 402 | Panasonic | Digikey | P0.0JTR-ND | 0.1W
93 | R41 | 0 | 402 | Panasonic | Digikey | P0.0JTR-ND | 0.1W
94 | R42 | 0 | 402 | Panasonic | Digikey | P0.0JTR-ND | 0.1W
95 | R43 | 0 | 402 | Panasonic | Digikey | P0.0JTR-ND | 0.1W
96 | U1 | OMNETICS-36-Dual | OMNETICS-36-Dual | Omnetics |  | A79025-001
97 | U2 | OMNETICS-36-Dual | OMNETICS-36-Dual | Omnetics |  | A79025-001
98 | U3 | RHD2132 | QFN-56 | Intan | Tech |  | D8214
99 | U4 | RHD2132 | QFN-56 | Intan | Tech |  | D8214
100 | U5 | OMNETICS-36-Dual | OMNETICS-36-Dual | Omnetics |  | A79025-001
101 | U6 | OMNETICS-36-Dual | OMNETICS-36-Dual | Omnetics |  | A79025-001
102 | U7 | RHD2132 | QFN-56 | Intan | Tech |  | D8214
103 | U8 | RHD2132 | QFN-56 | Intan | Tech |  | D8214
104 | U9 | -/+ | 2x100mil
105 | U10 | TPS62410DRCR | QFN-10 | Texas | Instrument | Digikey | 296-25488-1-ND
106 | U11 | ABM10XTAL | ABM10 | Abracon | Digikey | 535-10923-1-ND | 16MHz+/-20ppm, 30ppm stability, 150 Ohm ESR
107 | U12 | BF532-160 | CSP_BGA160 | Analog | Devices | Digikey | ADSP-BF532SBBCZ400-ND | 400MHz
108 | U13 | NRF24L01 | QFN-20 | Nordic | Semi | Mouser | 949-NRF24L01P-R
109 | U14 | MAX6711T | SC-70-4 | Maxim | Digikey | MAX6711TEXS+TCT-ND | Threshold | Voltage | = | 3.08V
110 | U15 | SST25VF040B-80-4I-SAE | SOIC-8 | Microchip | Mouser | 804-25VF040B8ISAE
111 | U16 | OMNETICS-9x100 | OMNETICS-9x100
112 | U17 | Multilayer Chip antenna | 748891025 | Wurth | Digikey | 732-1838-1-ND | 2.4-2.5GHz; VSWR=2; Gain=3dB; Marked spot toward board
113 | U18 | OMNETICS-9x100 | OMNETICS-9x100

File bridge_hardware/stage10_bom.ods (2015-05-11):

value | footprint | count | Digi-key | references
0.1uf | 402 | 51 | 490-1318-1-ND (http://search.digikey.com/us/en/products/GRM155R61A104KA01D/490-1318-1-ND/587923) | C64 C63 C76 C81 C2 C38 C12 C9 C14 C15 C50 C56 C55 C37 C33 C8 C6 C10 C11 C42 C36 C31 C28 C26 C49 C47 C13 C46
200 | 402 | 41 | P200JCT-ND (http://search.digikey.com/us/en/products/ERJ-2GEJ201X/P200JCT-ND/146925) | R41 R40 R42 R35 R36 R53 R52 R54 R47 R48 R65 R64 R66 R59 R60 R77 R76 R78 R71 R72 R79 R80
2.2uf | 402 | 22 | 445-6847-1-ND (http://search.digikey.com/us/en/products/C1005X5R0J225K/445-6847-1-ND/2619209) | C37 C36 C35 C38 C42 C45 C44 C43 C46 C50 C53 C52 C51 C54 C58 C61 C60 C59 C62 C66
1uf | 402 | 21 | 490-3890-1-ND (http://search.digikey.com/us/en/products/GRM155R61A105KE15D/490-3890-1-ND/965932) | C69 C66 C72 C85 C91 C40 C18 C7 C48 C32 C5 C3 C60 C39 C41 C61 C62 C73
130 | 402 | 20 | P130JCT-ND (http://search.digikey.com/us/en/products/ERJ-2GEJ131X/P130JCT-ND/146865) | R36 R37 R42 R43 R44 R45 R46 R47 R48 R49 R104 R107 R105 R108 R106 R109 R103 R114 R132 R133
50k | 402 | 15 | P49.9KLCT-ND (http://search.digikey.com/us/en/products/ERJ-2RKF4992X/P49.9KLCT-ND/194427) | R8 R21 R22 R23 R18 R24 R19 R20 R25 R29 R30 R50 R51 R53 R55
22k | 402 | 14 | P22KJCT-ND (http://search.digikey.com/us/en/products/ERJ-2GEJ223X/P22KJCT-ND/146939) | R30 R21 R17 R26 R29 R23 R81 R82
10k | 402 | 10 | P10KJCT-ND (http://search.digikey.com/us/en/products/ERJ-2GEJ103X/P10KJCT-ND/146734) | R41 R26 R27 R28 R15 R17 R128 R115 R134 R135
33 | 402 | 9 | P33JCT-ND (http://search.digikey.com/us/en/products/ERJ-2GEJ330X/P33JCT-ND/146979) | R16 R2 R1 R7 R52 R13 R14 R54 R56
0.01uf | 402 | 6 | 490-1312-1-ND (http://search.digikey.com/us/en/products/GRM155R71E103KA01D/490-1312-1-ND/587934) | C35 C30 C27 C25
49.9 | 402 | 5 | P49.9LCT-ND (http://search.digikey.com/us/en/products/ERJ-2RKF49R9X/P49.9LCT-ND/194426) | R35 R34 R33 R32 R121
24.9k | 402 | 5 | P24.9KLCT-ND (http://search.digikey.com/us/en/products/ERJ-2RKF2492X/P24.9KLCT-ND/194285) | R120 R38 R50 R62 R74
15k | 402 | 4 | P15KJCT-ND (http://search.digikey.com/us/en/products/ERJ-2GEJ153X/P15KJCT-ND/146879) | R37 R49 R61 R73
5k | 402 | 4 | P4.99KLCT-ND (http://search.digikey.com/us/en/products/ERJ-2RKF4991X/P4.99KLCT-ND/194389) | R74 R73 R76 R75
7k | 402 | 5 | P6.98KLCT-ND (http://search.digikey.com/us/en/products/ERJ-2RKF6981X/P6.98KLCT-ND/194470) | R39 R51 R63 R75 R129
7pf | 402 | 4 | 490-3107-1-ND (http://search.digikey.com/us/en/products/GJM1555C1H7R0CB01D/490-3107-1-ND/702373) | C16 C23 C22 C21
0.001uf | 402 | 5 | 490-1303-1-ND | C26 C24 C23 C68 C67 ** incorrect p/n originally.
100pf | 402 | 3 | 445-6845-1-ND (http://search.digikey.com/us/en/products/C1005C0G1E101J/445-6845-1-ND/2619207) | C75 C87 C51
15pf | 402 | 3 | 490-1280-1-ND (http://search.digikey.com/us/en/products/GRM1555C1H150JZ01D/490-1280-1-ND/587885) | C54 C53 C52
ferrite | 402 | 3 | 490-1006-1-ND (http://search.digikey.com/us/en/products/BLM15AG601SN1D/490-1006-1-ND/584454) | L3 L4 L6
402 | 402 | 2 | P402LCT-ND (http://search.digikey.com/us/en/products/ERJ-2RKF4020X/P402LCT-ND/194392) | R126 R122
33pf | 402 | 2 | 490-3220-1-ND (http://search.digikey.com/us/en/products/GRM1555C1H330JZ01D/490-3220-1-ND/702761) | C17 C11
4.7pF | 402 | 2 | 490-3100-1-ND (http://search.digikey.com/us/en/products/GJM1555C1H4R7CB01D/490-3100-1-ND/702366) | C17 C28
47pf | 402 | 2 | 490-1287-1-ND (http://search.digikey.com/us/en/products/GRM1555C1H470JZ01D/490-1287-1-ND/587893) | C74 C77
80k | 402 | 2 | P80.6KLCT-ND (http://search.digikey.com/us/en/products/ERJ-2RKF8062X/P80.6KLCT-ND/194532) | R117 R118
90k | 402 | 2 | P90.9KLCT-ND (http://search.digikey.com/us/en/products/ERJ-2RKF9092X/P90.9KLCT-ND/194556) | R5 R6
1.27k | 402 | 1 | P1.27KLCT-ND (http://search.digikey.com/us/en/products/ERJ-2RKF1271X/P1.27KLCT-ND/194098) | R119
1.5pF | 402 | 1 | 478-5992-1-ND (http://search.digikey.com/us/en/products/04025U1R5BAT2A/478-5992-1-ND/2208917) | C29
12.1k | 402 | 1 | P12.1KLCT-ND (http://search.digikey.com/us/en/products/ERJ-2RKF1212X/P12.1KLCT-ND/79807) | R31
13.3k | 402 | 1 | P13.3KLCT-ND (http://search.digikey.com/us/en/products/ERJ-2RKF1332X/P13.3KLCT-ND/194165) | R131
165k | 402 | 1 | P165KLCT-ND (http://search.digikey.com/us/en/products/ERJ-2RKF1653X/P165KLCT-ND/194205) | R15
180k | 402 | 1 | P180KJCT-ND (http://search.digikey.com/us/en/products/ERJ-2GEJ184X/P180KJCT-ND/146891) | R3
1pF | 402 | 1 | 490-3083-1-ND (http://search.digikey.com/us/en/products/GJM1555C1H1R0CB01D/490-3083-1-ND/702349) | C31
2.2nF | 402 | 1 | 490-1305-1-ND (http://search.digikey.com/us/en/products/GRM155R71H222KA01D/490-1305-1-ND/587945) | C32
2.7nH | 402 | 1 | PCD1851CT-ND (http://search.digikey.com/us/en/products/ELJ-QF2N7DF/PCD1851CT-ND/674200) | L5
200k | 402 | 1 | P200KJCT-ND (http://search.digikey.com/us/en/products/ERJ-2GEJ204X/P200KJCT-ND/146927) | R13
270k | 402 | 1 | P270KJCT-ND (http://search.digikey.com/us/en/products/ERJ-2GEJ274X/P270KJCT-ND/146951) | R16
2k | 402 | 1 | P2.0KJCT-ND (http://search.digikey.com/us/en/products/ERJ-2GEJ202X/P2.0KJCT-ND/146957) | R124
3.9nH | 402 | 1 | 732-1711-1-ND (http://search.digikey.com/us/en/products/744765039A/732-1711-1-ND/1994291) | L4
41.2k | 402 | 1 | P41.2KLCT-ND (http://search.digikey.com/us/en/products/ERJ-2RKF4122X/P41.2KLCT-ND/194395) | R130
47nf | 402 | 2 | 490-3270-1-ND (http://search.digikey.com/us/en/products/GRM155F51E473ZA01D/490-3270-1-ND/702811) | C82 C25
59k | 402 | 1 | P59.0KLCT-ND (http://search.digikey.com/us/en/products/ERJ-2RKF5902X/P59.0KLCT-ND/194461) | R116
6.8nf | 402 | 1 | 445-4922-1-ND (http://search.digikey.com/us/en/products/C1005X7R1H682K/445-4922-1-ND/2093536) | C88
725k | 402 | 1 | P732KLCT-ND (http://search.digikey.com/us/en/products/ERJ-2RKF7323X/P732KLCT-ND/194512) | R14
7pf | 402 | 1 | 490-3107-1-ND (http://search.digikey.com/us/en/products/GJM1555C1H7R0CB01D/490-3107-1-ND/702373) | C14
8.2nH | 402 | 1 | 732-1719-1-ND (http://search.digikey.com/us/en/products/744765082A/732-1719-1-ND/1994299) | L3
810k | 402 | 1 | P806KLCT-ND (http://search.digikey.com/us/en/products/ERJ-2RKF8063X/P806KLCT-ND/194534) | R4
10uf | 603 | 14 | 587-2562-1-ND (http://search.digikey.com/us/en/products/LMK107BJ106MALTD/587-2562-1-ND/2269355) | C65 C19 C20 C4 C43 C29 C45 C44
49.9 | 603 | 1 | 541-49.9SCT-ND (http://search.digikey.com/us/en/products/CRCW060349R9FKEAHP/541-49.9SCT-ND/2222759) | R127
50k | 603 | 1 | PNM0603-50KBCT-ND | R123
475-2558 | D0603 | 17 | 475-2558-1-ND (http://search.digikey.com/us/en/products/LY%20Q976-P1S2-36/475-2558-1-ND/1802685) | D36 D34 D32 D30 D28 D26 D24 D22 D35 D33 D31 D29 D27 D25 D23 D1
MAX6711Z | SC-70-4 | 2 | MAX6711ZEXS+TCT-ND (http://search.digikey.com/us/en/products/MAX6711ZEXS%2BT/MAX6711ZEXS%2BTCT-ND/1173297)
MIC5365-2.7 | SC-70-5 | 4 | 576-3319-1-ND (http://search.digikey.com/us/en/products/MIC5365-2.7YC5%20TR/576-3319-1-ND/1974137) | U15 U22 U29 U36
TC1016-3.0 | SC-70-5 | 4 | TC1016-3.0VLTCT-ND (http://search.digikey.com/us/en/products/TC1016-3.0VLTTR/TC1016-3.0VLTCT-ND/669507) | U16 U23 U30 U37
MIC5365-2.5 | SC-70-5 | 2 | 576-3185-1-ND (http://search.digikey.com/us/en/products/MIC5365-2.5YC5%20TR/576-3185-1-ND/1868222) | U14 U27
BAS16 | SOT-23 | 2 | 568-7979-1-ND (http://search.digikey.com/us/en/products/BAS16,235/568-7979-1-ND/2762669) | D19 D20
TLV431ACD | SOT-23 | 1 | 296-18912-1-ND (http://search.digikey.com/us/en/products/TLV431ACDBZR/296-18912-1-ND/863991) | U41
ADCS7476 | SOT-23-6 | 4 | ADCS7476AIMFCT-ND (http://search.digikey.com/us/en/products/ADCS7476AIMF%2FNOPB/ADCS7476AIMFCT-ND/568525) | U19 U26 U33 U40
FDC2512 | SOT-23-6 | 1 | FDC2512CT-ND (http://search.digikey.com/us/en/products/FDC2512/FDC2512CT-ND/2094414) | U38
USBLC6 | SOT-23-6 | 1 | 497-5235-6-ND | U11
** Hand-place SMD **
0.01uf | 805 | 1 | 478-6356-1-ND (http://search.digikey.com/us/en/products/08052C103KAZ2A/478-6356-1-ND/2512192) | C83
47uf | 1206 | 2 | 445-6003-1-ND (http://search.digikey.com/us/en/products/C3216X5R1C476M/445-6003-1-ND/2444044) | C90 C89
0.56 | 1206 | 1 | RL16R.56FCT-ND (http://search.digikey.com/us/en/products/RL1632R-R560-F/RL16R.56FCT-ND/714532) | R125
4.7uf | 1210 | 5 | 445-6042-1-ND (http://search.digikey.com/us/en/products/C3225X7S2A475K/445-6042-1-ND/2444083) | C80 C86 C84 C78 C93
2.2uh | 1210 | 4 | 587-2165-6-ND (http://search.digikey.com/us/en/products/BRL3225T2R2M/587-2165-6-ND/2002956) | L1 L2
4.7uh | 1210 | 1 | 587-1624-1-ND (http://search.digikey.com/us/en/products/CBC3225T4R7MR/587-1624-1-ND/1008239) | L5
150uf | 2917 | 3 | 495-2225-1-ND (http://search.digikey.com/us/en/products/B45196H2157M409/495-2225-1-ND/770391) | C70 C71 C1
ABM10XTAL-16 | ABM10 | 1 | 535-10923-1-ND (http://search.digikey.com/us/en/products/ABM10-16.000MHZ-D30-T3/535-10923-1-ND/2624174) | U5
ABM10XTAL-24 | ABM10 | 1 | 535-9622-1-ND (http://search.digikey.com/us/en/products/ABM10-24.000MHZ-8-7-A15-T/535-9622-1-ND/1237089) | U12
ABM10XTAL-25 | ABM10 | 1 | 535-9095-1-ND (http://search.digikey.com/us/en/products/ABM10-25.000MHZ-E20-T/535-9095-1-ND/675612) | U9
ANTENNA | chip_ant | 1 |  | U12
MBRS540T3 | DO-214AC | 1 | SS16FSCT-ND (http://search.digikey.com/us/en/products/SS16/SS16FSCT-ND/2053174) | D21
MURA120 | DO-214AC | 1 | MURA120T3GOSCT-ND (http://search.digikey.com/us/en/products/MURA120T3G/MURA120T3GOSCT-ND/1139949) | D18
SMAJ58A | DO-214AC | 1 | SMAJ58ABCT-ND (http://search.digikey.com/us/en/products/SMAJ58A/SMAJ58ABCT-ND/2253531) | D17
BF532-160 | MBGA-160 | 1 | ADSP-BF532SBBCZ400-ND (http://search.digikey.com/us/en/products/ADSP-BF532SBBCZ400/ADSP-BF532SBBCZ400-ND/936535) | U6
BF527 | MBGA-208 | 1 | ADSP-BF527KBCZ-6A-ND (http://search.digikey.com/us/en/products/ADSP-BF527KBCZ-6A/ADSP-BF527KBCZ-6A-ND/2077092) | U13
AD5663 | MSOP-10 | 1 | AD5663ARMZ-ND (http://search.digikey.com/us/en/products/AD5663ARMZ/AD5663ARMZ-ND/1120031) | U28
OMNETICS_36 | omnetics_36_dual | 4 |  | U14 U21 U28 U35
9X100 | omnetics_9 | 12 |  | U18 U20 U25 U27 U32 U34 U39 U41 U3
TPS62410 | QFN-10 | 2 | 296-25488-1-ND (http://search.digikey.com/us/en/products/TPS62410DRCR/296-25488-1-ND/2193060) | U4
NRF24L01 | QFN-20 | 1 |  | U8
LAN8710A | QFN-32 | 1 | 638-1083-ND | U17
RHA2132 | QFN-56 | 4 |  | U42 U43 U44 U45
LM4808 | SOIC-8 | 1 | LM4808M-ND | U29
SST25VF040B | SOIC-8 | 2 | SST25VF040B-80-4I-SAE-ND (http://search.digikey.com/us/en/products/SST25VF040B-80-4I-SAE/SST25VF040B-80-4I-SAE-ND/2299395) | U15
TPS23753 | TSSOP-14 | 1 | 296-23547-5-ND (http://search.digikey.com/us/en/products/TPS23753PW/296-23547-5-ND/1880904) | U37
ADM3202 | TSSOP-16 | 1 | ADM3202ARUZ-ND (http://search.digikey.com/us/en/products/ADM3202ARUZ/ADM3202ARUZ-ND/820172) | U3
74LCX541 | TSSOP-20 | 4 | 74LCX541MTCXCT-ND (http://search.digikey.com/us/en/products/74LCX541MTCX/74LCX541MTCXCT-ND/965512) | U18 U23 U22 U33
MT48LC16M16A2 | VFBGA-54 | 1 | 557-1220-1-ND (http://search.digikey.com/us/en/products/MT48LC16M16A2BG-7E:D%20TR/557-1220-1-ND/1531201) | U7
** Through-hole **
POE13W | POE13W | 1 | 513-1105-1-ND (http://search.digikey.com/us/en/products/POE13W3X5.0-R/513-1105-1-ND/754612) | U40
POE-JACK | POE-JACK | 1 | A99645-ND | U36
NRF24L01-BREAK | 8x100mil | 5 | 609-3406-ND (http://search.digikey.com/us/en/products/68002-408HLF/609-3406-ND/1487482) | U24 U25 U26 U21 U35
ADSP_JTAG_CON | 7x2x100 | 2 | A26576-ND (http://search.digikey.com/us/en/products/87215-4/A26576-ND/298249) | U16 U34
63uf | 2x200mil | 1 | 493-1665-ND | C92
EN_VCC | 2x100mil | 4 | A26543-ND (http://search.digikey.com/us/en/products/87224-2/A26543-ND/298247) | U8
FOD817A | DIP-4 | 1 | FOD817A-ND (http://search.digikey.com/us/en/products/FOD817A/FOD817A-ND/1049821) | U39
RS232_CON | DB9 | 1 | A32115-ND | U1
GT12 | GT12MABE | 1 | CKN9048-ND
FCI_USB_B | FCI_USB_B | 1 | 609-1039-ND | U6
NHD-0216KZW | NHD-0216KZW | 1 | NHD-0216KZW-AB5-ND (http://search.digikey.com/us/en/products/NHD-0216KZW-AB5/NHD-0216KZW-AB5-ND/2626456)

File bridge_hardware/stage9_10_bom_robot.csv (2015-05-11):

value | footprint | count
0.1uf | 402 | 51
200 | 402 | 41
2.2uf | 402 | 22
1uf | 402 | 21
130 | 402 | 20
50k | 402 | 15
22k | 402 | 14
10k | 402 | 10
33 | 402 | 9
0.01uf | 402 | 6
49.9 | 402 | 5
24.9k | 402 | 5
15k | 402 | 4
5k | 402 | 4
7k | 402 | 5
7pf | 402 | 4
0.001uf | 402 | 5
100pf | 402 | 3
15pf | 402 | 3
ferrite | 402 | 3
402 | 402 | 2
33pf | 402 | 2
4.7pF | 402 | 2
47pf | 402 | 2
80k | 402 | 2
90k | 402 | 2
1.27k | 402 | 1
1.5pF | 402 | 1
12.1k | 402 | 1
13.3k | 402 | 1
165k | 402 | 1
180k | 402 | 1
1pF | 402 | 1
2.2nF | 402 | 1
2.7nH | 402 | 1
200k | 402 | 1
270k | 402 | 1
2k | 402 | 1
3.9nH | 402 | 1
41.2k | 402 | 1
47nf | 402 | 2
59k | 402 | 1
6.8nf | 402 | 1
725k | 402 | 1
7pf | 402 | 1
8.2nH | 402 | 1
810k | 402 | 1
10uf | 603 | 14
49.9 | 603 | 1
50k | 603 | 1
475-2558 | D0603 | 17
MAX6711Z | SC-70-4 | 2
MIC5365-2.7 | SC-70-5 | 4
TC1016-3.0 | SC-70-5 | 4
MIC5365-2.5 | SC-70-5 | 2
BAS16 | SOT-23 | 2
TLV431ACD | SOT-23 | 1
ADCS7476 | SOT-23-6 | 4
FDC2512 | SOT-23-6 | 1
USBLC6 | SOT-23-6 | 1

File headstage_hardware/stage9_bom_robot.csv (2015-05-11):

value | footprint | count | references
0.1uf | 402 | 23 | C41 C40 C39 C49 C48 C47 C57 C56 C55 C65 C64 C63 C3 C8 C16 C18 C19 C20 C21 C22 C4 C2 C68
200 | 402 | 22 | R41 R40 R42 R35 R36 R53 R52 R54 R47 R48 R65 R64 R66 R59 R60 R77 R76 R78 R71 R72 R79 R80
2.2uf | 402 | 20 | C37 C36 C35 C38 C42 C45 C44 C43 C46 C50 C53 C52 C51 C54 C58 C61 C60 C59 C62 C66
22k | 402 | 9 | R30 R28 R21 R17 R26 R29 R23 R81 R82
15k | 402 | 4 | R37 R49 R61 R73
24.9k | 402 | 4 | R38 R50 R62 R74
7k | 402 | 4 | R39 R51 R63 R75
0.001uf | 402 | 3 | C26 C24 C23
1uf | 402 | 3 | C30 C9 C67
0.01uf | 402 | 2 | C27 C7
4.7pF | 402 | 2 | C17 C28
1.5pF | 402 | 1 | C29
165k | 402 | 1 | R15
1pF | 402 | 1 | C31
2.2nF | 402 | 1 | C32
2.7nH | 402 | 1 | L5
200k | 402 | 1 | R13
270k | 402 | 1 | R16 | 1 | Designed in Kicadocaml
3.9nH | 402 | 1 | L4
33pf | 402 | 1 | C11
47nf | 402 | 1 | C25
725k | 402 | 1 | R14
7pf | 402 | 1 | C14
8.2nH | 402 | 1 | L3
ferrite | 402 | 1 | L6
10uf | 603 | 6 | C12 C13 C6 C10 C15 C1
LED | D0603 | 1 | D1
MAX6711Z | SC-70-4 | 1 | U11
MIC5365-2.7 | SC-70-5 | 4 | U15 U22 U29 U36
TC1016-3.0 | SC-70-5 | 4 | U16 U23 U30 U37
ADCS7476 | SOT-23-6 | 4 | U19 U26 U33 U40

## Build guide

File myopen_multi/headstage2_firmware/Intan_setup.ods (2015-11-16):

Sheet: Sheet1
@end of | ADC Activity | MOSI | MISO | FIFO
call1 | ??? | reg0 | ??? | reg1, reg2, reg3, reg4
call2 | write reg0 | reg1 | ??? | reg2, reg3, reg4, reg5
call3 | write reg1 | reg2 | reg0 out | reg3, reg4, reg5, reg6
call4 | write reg2 | reg3 | reg1 out | reg4, reg5, reg6, reg7
call5 | write reg3 | reg4 | reg2 out | reg5, reg6, reg7, reg8
call6 | write reg4 | reg5 | reg3 out | reg6, reg7, reg8, reg9
call7 | write reg5 | reg6 | reg4 out | reg7, reg8, reg9, reg10
call8 | write reg6 | reg7 | reg5 out | reg8, reg9, reg10, reg11
call9 | write reg7 | reg8 | reg6 out | reg9, reg10, reg11, reg12
call10 | write reg8 | reg9 | reg7 out | reg10, reg11, reg12, reg13
call11 | write reg9 | reg10 | reg8 out | reg11, reg12, reg13, reg14
call12 | write reg10 | reg11 | reg9 out | reg12, reg13, reg14, reg15
call13 | write reg11 | reg12 | reg10 out | reg13, reg14, reg15, reg16
call14 | write reg12 | reg13 | reg11 out | reg14, reg15, reg16, reg17
call15 | write reg13 | reg14 | reg12 out | reg15, reg16, reg17, amp#
call16 | write reg14 | reg15 | reg13 out | reg16, reg17, amp#, amp#
call17 | write reg15 | reg16 | reg14 out | reg17, amp#, amp#, amp# | fast_settle_loop iter1
call18 | write reg16 | reg17 | reg15 out | amp#, amp#, amp#, amp#
call19 | write reg17 | amp# | reg16 out | amp#, amp#, amp#, amp#
call20 | amp# | amp# | reg17 out | amp#, amp#, amp#, amp#
call21 | amp# | amp# | 32 | amp#, amp#, amp#, amp#
call22 | amp# | amp# | 32 | amp#, amp#, amp#, amp#
call23 | amp# | amp# | 32 | amp#, amp#, amp#, amp#
call24 | amp# | amp# | 32 | amp#, amp#, amp#, amp#
call25 | amp# | amp# | 32 | amp#, amp#, amp#, amp#
call26 | amp# | amp# | 32 | amp#, amp#, amp#, amp#
call27 | amp# | amp# | 32 | amp#, amp#, amp#, amp#
call28 | amp# | amp# | 32 | amp#, amp#, amp#, amp#
call29 | amp# | amp# | 32 | amp#, amp#, amp#, amp#
call30 | amp# | amp# | 32 | amp#, amp#, amp#, amp#
call31 | amp# | amp# | 32 | amp#, amp#, amp#, amp#
call32 | amp# | amp# | 32 | amp#, amp#, amp#, amp#
call33 | amp# | amp# | 32 | amp#, amp#, amp#, amp#
call34 | amp# | amp# | 32 | amp#, amp#, amp#, amp#
call35 | amp# | amp# | 32 | amp#, amp#, amp#, amp#
call36 | amp# | amp# | 32 | amp#, amp#, amp#, amp#
call37 | amp# | amp# | 32 | amp#, amp#, amp#, amp#
call38 | amp# | amp# | 32 | amp#, amp#, amp#, amp#
call39 | amp# | amp# | 32 | amp#, amp#, amp#, amp#
call40 | amp# | amp# | 32 | amp#, amp#, amp#, amp#
call41 | amp# | amp# | 32 | amp#, amp#, amp#, amp#
call42 | amp# | amp# | 32 | amp#, amp#, amp#, amp#
call43 | amp# | amp# | 32 | amp#, amp#, amp#, amp#
call44 | amp# | amp# | 32 | amp#, amp#, amp#, amp#
call45 | amp# | amp# | 32 | amp#, amp#, amp#, amp#
call46 | amp# | amp# | 32 | amp#, amp#, amp#, amp#
call47 | amp# | amp# | 32 | amp#, amp#, amp#, amp#
call48 | amp# | amp# | 32 | amp#, amp#, amp#, amp#
call49 | amp# | amp# | 32 | amp#, amp#, amp#, amp#
call50 | amp# | amp# | 32 | amp#, amp#, amp#, amp#
call51 | amp# | amp# | 32 | amp#, amp#, amp#, amp#
call52 | amp# | amp# | 32 | amp#, amp#, amp#, amp#
call53 | amp# | amp# | 32 | amp#, amp#, amp#, amp#
call54 | amp# | amp# | 32 | amp#, amp#, amp#, amp#
call55 | amp# | amp# | 32 | amp#, amp#, amp#, amp#
call56 | amp# | amp# | 32 | amp#, amp#, amp#, amp#
call57 | amp# | amp# | 32 | amp#, amp#, amp#, amp#
call58 | amp# | amp# | 32 | amp#, amp#, amp#, amp#
call59 | amp# | amp# | 32 | amp#, amp#, amp#, amp#
call60 | amp# | amp# | 32 | amp#, amp#, amp#, amp#
call61 | amp# | amp# | 32 | amp#, amp#, amp#, amp#
call62 | amp# | amp# | 32 | amp#, amp#, amp#, amp#
call63 | amp# | amp# | 32 | amp#, amp#, amp#, amp#
call64 | amp# | amp# | 32 | amp#, amp#, amp#, amp#
call65 | amp# | amp# | 32 | amp#, amp#, amp#, amp#
call66 | amp# | amp# | 32 | amp#, amp#, amp#, amp#
call67 | amp# | amp# | 32 | amp#, amp#, amp#, amp#
call68 | amp# | amp# | 32 | amp#, amp#, amp#, amp#
call69 | amp# | amp# | 32 | amp#, amp#, amp#, amp#
call70 | amp# | amp# | 32 | amp#, amp#, amp#, amp#
call71 | amp# | amp# | 32 | amp#, amp#, amp#, amp#
call72 | amp# | amp# | 32 | amp#, amp#, amp#, amp#
call73 | amp# | amp# | 32 | amp#, amp#, amp#, amp#
call74 | amp# | amp# | 32 | amp#, amp#, amp#, amp#
call75 | amp# | amp# | 32 | amp#, amp#, amp#, amp#
call76 | amp# | amp# | 32 | amp#, amp#, amp#, amp#
call77 | amp# | amp# | 32 | amp#, amp#, amp#, amp#
call78 | amp# | amp# | 32 | amp#, amp#, amp#, amp#
call79 | amp# | amp# | 32 | amp#, amp#, amp#, amp#
call80 | amp# | amp# | 32 | amp#, amp#, amp#, amp#
call81 | amp# | amp# | 32 | amp#, amp#, amp#, amp#
call82 | amp# | amp# | 32 | amp#, amp#, amp#, amp#
call83 | amp# | amp# | 32 | amp#, amp#, amp#, amp#
call84 | amp# | amp# | 32 | amp#, amp#, amp#, amp#
call85 | amp# | amp# | 32 | amp#, amp#, amp#, amp#
call86 | amp# | amp# | 32 | amp#, amp#, amp#, amp#
call87 | amp# | amp# | 32 | amp#, amp#, amp#, amp#
call88 | amp# | amp# | 32 | amp#, amp#, amp#, amp#
call89 | amp# | amp# | 32 | amp#, amp#, amp#, amp#
call90 | amp# | amp# | 32 | amp#, amp#, amp#, amp#
call91 | amp# | amp# | 32 | amp#, amp#, amp#, amp#
call92 | amp# | amp# | 32 | amp#, amp#, amp#, amp#
call93 | amp# | amp# | 32 | amp#, amp#, amp#, amp#
call94 | amp# | amp# | 32 | amp#, amp#, amp#, amp#
call95 | amp# | amp# | 32 | amp#, amp#, amp#, amp#
call96 | amp# | amp# | 32 | amp#, amp#, amp#, amp#
call97 | amp# | amp# | 32 | amp#, amp#, amp#, amp#
call98 | amp# | amp# | 32 | amp#, amp#, amp#, amp#
call99 | amp# | amp# | 32 | amp#, amp#, amp#, amp#
call100 | amp# | amp# | 32 | amp#, amp#, amp#, amp#
call101 | amp# | amp# | 32 | amp#, amp#, amp#, amp#
call102 | amp# | amp# | 32 | amp#, amp#, amp#, amp#
call103 | amp# | amp# | 32 | amp#, amp#, amp#, amp#
call104 | amp# | amp# | 32 | amp#, amp#, amp#, amp#
call105 | amp# | amp# | 32 | amp#, amp#, amp#, amp#
call106 | amp# | amp# | 32 | amp#, amp#, amp#, amp#
call107 | amp# | amp# | 32 | amp#, amp#, amp#, amp#
call108 | amp# | amp# | 32 | amp#, amp#, amp#, amp#
call109 | amp# | amp# | 32 | amp#, amp#, amp#, amp#
call110 | amp# | amp# | 32 | amp#, amp#, amp#, amp#
call111 | amp# | amp# | 32 | amp#, amp#, amp#, amp#
call112 | amp# | amp# | 32 | amp#, amp#, amp#, amp#
call113 | amp# | amp# | 32 | amp#, amp#, amp#, amp#
call114 | amp# | amp# | 32 | amp#, amp#, amp#, amp#
call115 | amp# | amp# | 32 | amp#, amp#, amp#, amp#
call116 | amp# | amp# | 32 | amp#, amp#, amp#, amp#
call117 | amp# | amp# | 32 | amp#, amp#, amp#, amp#
call118 | amp# | amp# | 32 | amp#, amp#, amp#, amp#
call119 | amp# | amp# | 32 | amp#, amp#, amp#, amp#
call120 | amp# | amp# | 32 | amp#, amp#, amp#, amp#
call121 | amp# | amp# | 32 | amp#, amp#, amp#, amp#
call122 | amp# | amp# | 32 | amp#, amp#, amp#, amp#
call123 | amp# | amp# | 32 | amp#, amp#, amp#, amp#
call124 | amp# | amp# | 32 | amp#, amp#, amp#, amp#
call125 | amp# | amp# | 32 | amp#, amp#, amp#, amp#
call126 | amp# | amp# | 32 | amp#, amp#, amp#, amp#
call127 | amp# | amp# | 32 | amp#, amp#, amp#, amp#
call128 | amp# | amp# | 32 | amp#, amp#, amp#, amp#
call129 | amp# | amp# | 32 | amp#, amp#, amp#, amp#
call130 | amp# | amp# | 32 | amp#, amp#, amp#, amp#
call131 | amp# | amp# | 32 | amp#, amp#, amp#, amp#
call132 | amp# | amp# | 32 | amp#, amp#, amp#, amp#
call133 | amp# | amp# | 32 | amp#, amp#, amp#, amp#
call134 | amp# | amp# | 32 | amp#, amp#, amp#, amp#
call135 | amp# | amp# | 32 | amp#, amp#, amp#, amp#
call136 | amp# | amp# | 32 | amp#, amp#, amp#, amp#
call137 | amp# | amp# | 32 | amp#, amp#, amp#, amp#
call138 | amp# | amp# | 32 | amp#, amp#, amp#, amp#
call139 | amp# | amp# | 32 | amp#, amp#, amp#, amp#
call140 | amp# | amp# | 32 | amp#, amp#, amp#, amp#
call141 | amp# | amp# | 32 | amp#, amp#, amp#, amp#
call142 | amp# | amp# | 32 | amp#, amp#, amp#, amp#
call143 | amp# | amp# | 32 | amp#, amp#, amp#, amp#
call144 | amp# | amp# | 32 | amp#, amp#, amp#, amp#
call145 | amp# | amp# | 32 | amp#, amp#, amp#, amp#
call146 | amp# | amp# | 32 | amp#, amp#, amp#, amp#
call147 | amp# | amp# | 32 | amp#, amp#, amp#, amp#
call148 | amp# | amp# | 32 | amp#, amp#, amp#, amp#
call149 | amp# | amp# | 32 | amp#, amp#, amp#, amp#
call150 | amp# | amp# | 32 | amp#, amp#, amp#, amp#
call151 | amp# | amp# | 32 | amp#, amp#, amp#, amp#
call152 | amp# | amp# | 32 | amp#, amp#, amp#, amp#
call153 | amp# | amp# | 32 | amp#, amp#, amp#, amp#
call154 | amp# | amp# | 32 | amp#, amp#, amp#, amp#
call155 | amp# | amp# | 32 | amp#, amp#, amp#, amp#
call156 | amp# | amp# | 32 | amp#, amp#, amp#, amp#
call157 | amp# | amp# | 32 | amp#, amp#, amp#, amp#
call158 | amp# | amp# | 32 | amp#, amp#, amp#, amp#
call159 | amp# | amp# | 32 | amp#, amp#, amp#, amp#
call160 | amp# | amp# | 32 | amp#, amp#, amp#, amp#
call161 | amp# | amp# | 32 | amp#, amp#, amp#, amp#
call162 | amp# | amp# | 32 | amp#, amp#, amp#, amp#
call163 | amp# | amp# | 32 | amp#, amp#, amp#, amp#
call164 | amp# | amp# | 32 | amp#, amp#, amp#, amp#
call165 | amp# | amp# | 32 | amp#, amp#, amp#, amp#
call166 | amp# | amp# | 32 | amp#, amp#, amp#, amp#
call167 | amp# | amp# | 32 | amp#, amp#, amp#, amp#
call168 | amp# | amp# | 32 | amp#, amp#, amp#, amp#
call169 | amp# | amp# | 32 | amp#, amp#, amp#, amp#
call170 | amp# | amp# | 32 | amp#, amp#, amp#, amp#
call171 | amp# | amp# | 32 | amp#, amp#, amp#, amp#
call172 | amp# | amp# | 32 | amp#, amp#, amp#, amp#
call173 | amp# | amp# | 32 | amp#, amp#, amp#, amp#
call174 | amp# | amp# | 32 | amp#, amp#, amp#, amp#
call175 | amp# | amp# | 32 | amp#, amp#, amp#, amp#
call176 | amp# | amp# | 32 | amp#, amp#, amp#, amp#
call177 | amp# | amp# | 32 | amp#, amp#, amp#, amp#
call178 | amp# | amp# | 32 | amp#, amp#, amp#, amp#
call179 | amp# | amp# | 32 | amp#, amp#, amp#, amp#
call180 | amp# | amp# | 32 | amp#, amp#, amp#, amp#
call181 | amp# | amp# | 32 | amp#, amp#, amp#, amp#
call182 | amp# | amp# | 32 | amp#, amp#, amp#, amp#
call183 | amp# | amp# | 32 | amp#, amp#, amp#, amp#
call184 | amp# | amp# | 32 | amp#, amp#, amp#, amp#
call185 | amp# | amp# | 32 | amp#, amp#, amp#, amp#
call186 | amp# | amp# | 32 | amp#, amp#, amp#, amp#
call187 | amp# | amp# | 32 | amp#, amp#, amp#, amp#
call188 | amp# | amp# | 32 | amp#, amp#, amp#, amp#
call189 | amp# | amp# | 32 | amp#, amp#, amp#, amp#
call190 | amp# | amp# | 32 | amp#, amp#, amp#, amp#
call191 | amp# | amp# | 32 | amp#, amp#, amp#, amp#
call192 | amp# | amp# | 32 | amp#, amp#, amp#, amp#
call193 | amp# | amp# | 32 | amp#, amp#, amp#, amp#
call194 | amp# | amp# | 32 | amp#, amp#, amp#, amp#
call195 | amp# | amp# | 32 | amp#, amp#, amp#, amp#
call196 | amp# | amp# | 32 | amp#, amp#, amp#, amp#
call197 | amp# | amp# | 32 | amp#, amp#, amp#, amp#
call198 | amp# | amp# | 32 | amp#, amp#, amp#, amp#
call199 | amp# | amp# | 32 | amp#, amp#, amp#, amp#
call200 | amp# | amp# | 32 | amp#, amp#, amp#, amp#
call201 | amp# | amp# | 32 | amp#, amp#, amp#, amp#
call202 | amp# | amp# | 32 | amp#, amp#, amp#, amp#
call203 | amp# | amp# | 32 | amp#, amp#, amp#, amp#
call204 | amp# | amp# | 32 | amp#, amp#, amp#, amp#
call205 | amp# | amp# | 32 | amp#, amp#, amp#, amp#
call206 | amp# | amp# | 32 | amp#, amp#, amp#, amp#
call207 | amp# | amp# | 32 | amp#, amp#, amp#, amp#
call208 | amp# | amp# | 32 | amp#, amp#, amp#, amp#
call209 | amp# | amp# | 32 | amp#, amp#, amp#, amp#
call210 | amp# | amp# | 32 | amp#, amp#, amp#, amp#
call211 | amp# | amp# | 32 | amp#, amp#, amp#, amp#
call212 | amp# | amp# | 32 | amp#, amp#, amp#, amp#
call213 | amp# | amp# | 32 | amp#, amp#, amp#, amp#
call214 | amp# | amp# | 32 | amp#, amp#, amp#, amp#
call215 | amp# | amp# | 32 | amp#, amp#, amp#, amp#
call216 | amp# | amp# | 32 | amp#, amp#, amp#, amp#
call217 | amp# | amp# | 32 | amp#, amp#, amp#, amp#
call218 | amp# | amp# | 32 | amp#, amp#, amp#, amp#
call219 | amp# | amp# | 32 | amp#, amp#, amp#, amp#
call220 | amp# | amp# | 32 | amp#, amp#, amp#, amp#
call221 | amp# | amp# | 32 | amp#, amp#, amp#, amp#
call222 | amp# | amp# | 32 | amp#, amp#, amp#, amp#
call223 | amp# | amp# | 32 | amp#, amp#, amp#, amp#
call224 | amp# | amp# | 32 | amp#, amp#, amp#, amp#
call225 | amp# | amp# | 32 | amp#, amp#, amp#, amp#
call226 | amp# | amp# | 32 | amp#, amp#, amp#, amp#
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

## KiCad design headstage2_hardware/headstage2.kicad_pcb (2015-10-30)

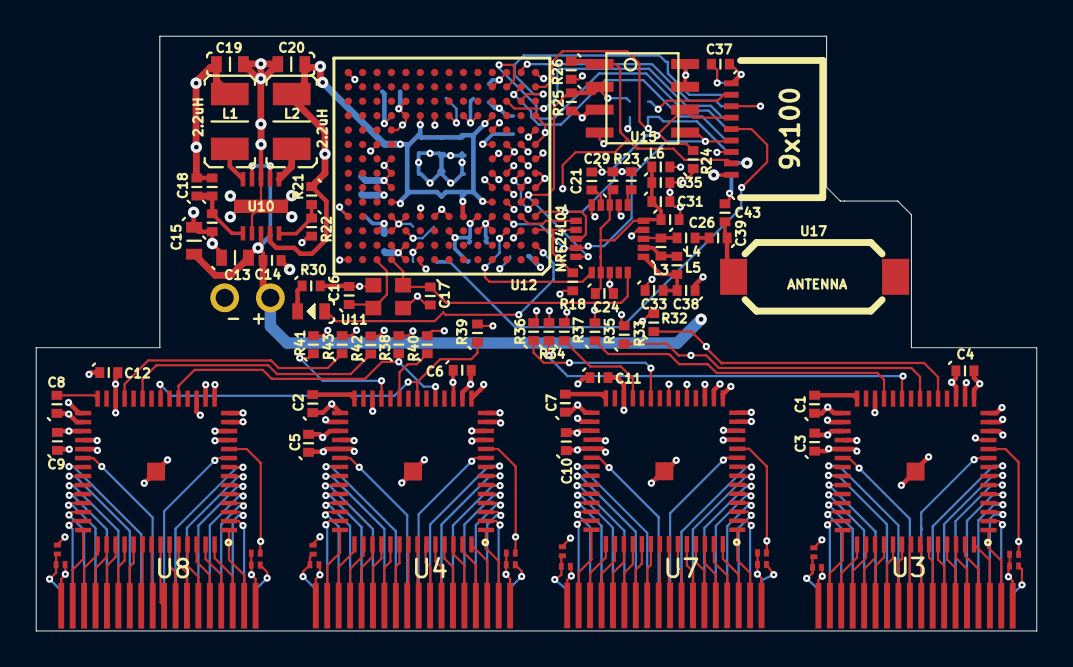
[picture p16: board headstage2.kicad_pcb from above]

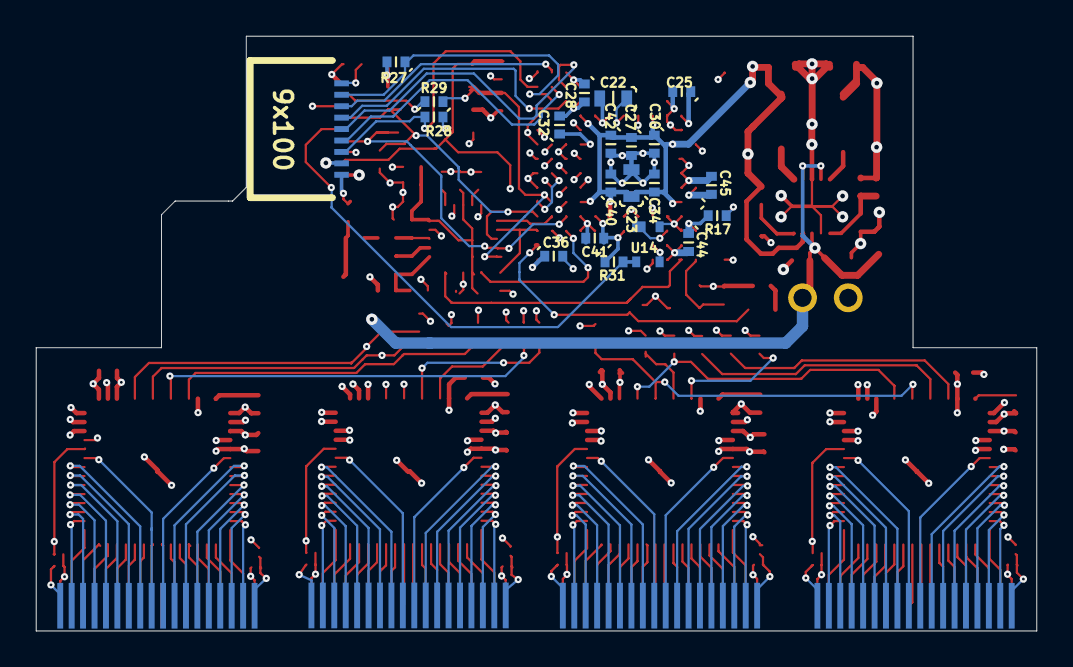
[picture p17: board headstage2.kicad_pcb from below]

Board: 6 copper layers, 55.6 x 33.0 mm, 113 parts (21 on the bottom side), 205 nets.

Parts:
C1, C2, C7, C8, C31, C42: 10nF; 0402
C3, C4, C5, C6, C9, C10, C11, C12: 100nF; 0402
C13, C15, C19, C20, C22, C23: 10uF; 0603
C14, C25, C28, C30, C32, C34, C36, C40, C41, C44, C45: 0.1uF; 0402
C16: 7pF; 0402
C17, C33: 4.7pF; 0402
C18: 33pF; 0402
C21: 47nF; 0402
C24, C26, C29: 1nF; 0402
C27, C35, C37: 1uF; 0402
C38: 2.2nF; 0402
C39: 1.5pF; 0402
C43: 1pF; 0402
D1: LED; D0603
L1, L2: 2.2uH; 1210
L3: 8.2nH; 0402
L4: 3.9nH; 0402
L5: 2.7nH; 0402
L6: Ferrite; 0402
R1, R2, R3, R4, R5, R6, R7, R8, R9, R10, R11, R12, R13, R14, R15, R16: 0; 0201
R17, R18, R23, R24, R25, R26, R27, R28, R31: 22K; 0402
R19: 200K; 0402
R20: 909k; 0402
R21: 165K; 0402
R22: 270K; 0402
R29, R30: 200; 0402
R32, R33, R34, R35, R36, R37, R38, R39, R40, R41, R42, R43: 0; 0402
U1, U2, U5, U6: OMNETICS_A79025; omnetics_36_dual
U3, U4, U7, U8: RHD2132; QFN-56
U9: - +; 2x100mil
U10: TPS62410; QFN-10
U11: ABM10XTAL; ABM10
U12: BF532-160; CSP_BGA-160
U13: NRF24L01; QFN-20
U14: MAX6711T; SC-70-4
U15: SST25VF040B; SOIC-8(SAE)
U16, U18: 9x100; omnetics_9
U17: ANTENNA; chip_ant

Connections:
+BATT: C13.2, C14.2, C15.2, C37.1, U9.2, U10.3, U10.7, U10.9, U16.1, U16.9, U18.8
/A_IN0: U1.B9, U3.9
/A_IN1: U1.B8, U3.8
/A_IN2: U1.B7, U3.7
/A_IN3: U1.B6, U3.6
/A_IN4: U1.B5, U3.5
/A_IN5: U1.B4, U3.4
/A_IN6: U1.B3, U3.3
/A_IN7: U1.B2, U3.2
/A_IN8: U1.T2, U3.1
/A_IN9: U1.T3, U3.56
/A_IN10: U1.T4, U3.55
/A_IN11: U1.T5, U3.54
/A_IN12: U1.T6, U3.53
/A_IN13: U1.T7, U3.52
/A_IN14: U1.T8, U3.51
/A_IN15: U1.T9, U3.50
/A_IN16: U1.T10, U3.49
/A_IN17: U1.T11, U3.48
/A_IN18: U1.T12, U3.47
/A_IN19: U1.T13, U3.46
/A_IN20: U1.T14, U3.45
/A_IN21: U1.T15, U3.44
/A_IN22: U1.T16, U3.43
/A_IN23: U1.T17, U3.42
/A_IN24: U1.B17, U3.41
/A_IN25: U1.B16, U3.40
/A_IN26: U1.B15, U3.39
/A_IN27: U1.B14, U3.38
/A_IN28: U1.B13, U3.37
/A_IN29: U1.B12, U3.36
/A_IN30: U1.B11, U3.35
/A_IN31: U1.B10, U3.34
/B_IN0: U5.B9, U7.9
/B_IN1: U5.B8, U7.8
/B_IN2: U5.B7, U7.7
/B_IN3: U5.B6, U7.6
/B_IN4: U5.B5, U7.5
/B_IN5: U5.B4, U7.4
/B_IN6: U5.B3, U7.3
/B_IN7: U5.B2, U7.2
/B_IN8: U5.T2, U7.1
/B_IN9: U5.T3, U7.56
/B_IN10: U5.T4, U7.55
/B_IN11: U5.T5, U7.54
/B_IN12: U5.T6, U7.53
/B_IN13: U5.T7, U7.52
/B_IN14: U5.T8, U7.51
/B_IN15: U5.T9, U7.50
/B_IN16: U5.T10, U7.49
/B_IN17: U5.T11, U7.48
/B_IN18: U5.T12, U7.47
/B_IN19: U5.T13, U7.46
/B_IN20: U5.T14, U7.45
/B_IN21: U5.T15, U7.44
/B_IN22: U5.T16, U7.43
/B_IN23: U5.T17, U7.42
/B_IN24: U5.B17, U7.41
/B_IN25: U5.B16, U7.40
/B_IN26: U5.B15, U7.39
/B_IN27: U5.B14, U7.38
/B_IN28: U5.B13, U7.37
/B_IN29: U5.B12, U7.36
/B_IN30: U5.B11, U7.35
/B_IN31: U5.B10, U7.34
/C_IN0: U2.B9, U4.9
/C_IN1: U2.B8, U4.8
/C_IN2: U2.B7, U4.7
/C_IN3: U2.B6, U4.6
/C_IN4: U2.B5, U4.5
/C_IN5: U2.B4, U4.4
/C_IN6: U2.B3, U4.3
/C_IN7: U2.B2, U4.2
/C_IN8: U2.T2, U4.1
/C_IN9: U2.T3, U4.56
/C_IN10: U2.T4, U4.55
/C_IN11: U2.T5, U4.54
/C_IN12: U2.T6, U4.53
/C_IN13: U2.T7, U4.52
/C_IN14: U2.T8, U4.51
/C_IN15: U2.T9, U4.50
/C_IN16: U2.T10, U4.49
/C_IN17: U2.T11, U4.48
/C_IN18: U2.T12, U4.47
/C_IN19: U2.T13, U4.46
/C_IN20: U2.T14, U4.45
/C_IN21: U2.T15, U4.44
/C_IN22: U2.T16, U4.43
/C_IN23: U2.T17, U4.42
/C_IN24: U2.B17, U4.41
/C_IN25: U2.B16, U4.40
/C_IN26: U2.B15, U4.39
/C_IN27: U2.B14, U4.38
/C_IN28: U2.B13, U4.37
/C_IN29: U2.B12, U4.36
/C_IN30: U2.B11, U4.35
/C_IN31: U2.B10, U4.34
/DR0PRI: R35.2, U12.K1
/DR0PRI_out: R35.1, U3.25
/DR0SEC: R37.2, U12.J2
/DR0SEC_out: R37.1, U7.25
/DR1PRI: R41.2, U12.G3
/DR1PRI_out: R41.1, U4.25
/DR1SEC: R43.2, U12.F3
/DR1SEC_out: R43.1, U8.25
/DT0PRI: R34.2, U12.H1
/DT0PRI_out: R34.1, U3.23
/DT0SEC: R36.2, U12.H2
/DT0SEC_out: R36.1, U7.23
/DT1PRI: R40.2, U12.F2
/DT1PRI_out: R40.1, U4.23
/DT1SEC: R42.2, U12.E3
/DT1SEC_out: R42.1, U8.23
/D_IN0: U6.B9, U8.9
/D_IN1: U6.B8, U8.8
/D_IN2: U6.B7, U8.7
/D_IN3: U6.B6, U8.6
/D_IN4: U6.B5, U8.5
/D_IN5: U6.B4, U8.4
/D_IN6: U6.B3, U8.3
/D_IN7: U6.B2, U8.2
/D_IN8: U6.T2, U8.1
/D_IN9: U6.T3, U8.56
/D_IN10: U6.T4, U8.55
/D_IN11: U6.T5, U8.54
/D_IN12: U6.T6, U8.53
/D_IN13: U6.T7, U8.52
/D_IN14: U6.T8, U8.51
/D_IN15: U6.T9, U8.50
/D_IN16: U6.T10, U8.49
/D_IN17: U6.T11, U8.48
/D_IN18: U6.T12, U8.47
/D_IN19: U6.T13, U8.46
/D_IN20: U6.T14, U8.45
/D_IN21: U6.T15, U8.44
/D_IN22: U6.T16, U8.43
/D_IN23: U6.T17, U8.42
/D_IN24: U6.B17, U8.41
/D_IN25: U6.B16, U8.40
/D_IN26: U6.B15, U8.39
/D_IN27: U6.B14, U8.38
/D_IN28: U6.B13, U8.37
/D_IN29: U6.B12, U8.36
/D_IN30: U6.B11, U8.35
/D_IN31: U6.B10, U8.34
/FSync0: R32.2, U12.H3, U12.J3
/FSync0_out: R32.1, U3.19, U7.19
/FSync1: R38.2, U12.E1, U12.G2
/FSync1_out: R38.1, U4.19, U8.19
/MISO: R25.1, R29.1, U12.E2, U13.5, U15.2
/MOSI: U12.D3, U13.4, U15.5, U16.4
/MR: R31.2, U14.3, U16.5
/PF0: U12.D2, U13.1
/PF1: R18.1, U12.C1, U13.2
/PF2: R26.1, U12.C2, U15.1, U16.2
/PF3: U12.C3, U13.6
/PF4: D1.2, U12.B1
/RESET: U12.C10, U14.2
/SCK: R24.2, U12.D1, U13.3, U15.6, U16.6
/SCLK0: R33.2, U12.J1, U12.L1
/SCLK0_out: R33.1, U3.21, U7.21
/SCLK1: R39.2, U12.F1, U12.G1
/SCLK1_out: R39.1, U4.21, U8.21
/TCK: U12.P2, U18.3
/TDI: U12.M3, U18.4
/TDO: U12.N3, U18.5
/TMS: U12.N2, U18.6
/XTAL: C17.1, U11.3, U12.A11, U13.10
/~EMU: R27.1, U12.M2, U18.2
/~trst: R28.1, U12.N1, U18.7
GND: C1.1, C2.1, C3.1, C4.1, C5.1, C6.1, C7.1, C8.1, C9.1, C10.1, C11.1, C12.1, C13.1, C14.1, C15.1, C16.2, C17.2, C19.2, C20.2, C21.1, C22.2, C23.2, C24.2, C25.2, C26.2, C27.2, C28.2, C29.2, C30.2, C31.2, C32.2, C33.1, C34.2, C35.2, C36.2, C37.2, C38.1, C40.2, C41.2, C42.2, C43.1, C44.2, C45.2, R3.1, R4.1, R5.2, R6.2, R11.1, R12.1, R13.2, R14.2, R19.1, R22.2, R23.1, R24.1, R28.2, R30.2, U1.B1, U1.T18, U2.B1, U2.T18, U3.11, U3.12, U3.17, U3.29, U3.30, U3.32, U3.33, U3.57, U4.11, U4.12, U4.17, U4.29, U4.30, U4.32, U4.33, U4.57, U5.B1, U5.T18, U6.B1, U6.T18, U7.11, U7.12, U7.17, U7.29, U7.30, U7.32, U7.33, U7.57, U8.11, U8.12, U8.17, U8.29, U8.30, U8.32, U8.33, U8.57, U9.1, U10.2, U10.8, U10.11, U11.2, U11.4, U12.A9, U12.A10, U12.A14, U12.B10, U12.B11, U12.C4, U12.C5, U12.C11, U12.D4, U12.D7, U12.D8, U12.D10, U12.D11, U12.F4, U12.F11, U12.G11, U12.H4, U12.H11, U12.K4, U12.K11, U12.L5, U12.L6, U12.L8, U12.L10, U12.M4, U12.M10, U12.P14, U13.8, U13.14, U13.17, U13.20, U14.1, U15.4, U16.3, U16.7, U18.1, U18.9
unnamed: C1.2, U3.28
unnamed: C2.2, U4.28
unnamed: C7.2, U7.28
unnamed: C8.2, U8.28
unnamed: C16.1, U11.1, U12.A12
unnamed: C18.1, R19.2, R20.1, U10.1
unnamed: C21.2, U13.19
unnamed: C24.1, C26.1, C29.1, C31.1, C35.1, L6.1, U13.7, U13.15, U13.18
unnamed: C33.2, C38.2, L5.2, U13.11
unnamed: C39.1, C43.2, U17.1
unnamed: C39.2, L4.2
unnamed: D1.1, R30.1
unnamed: L1.2, U10.10
unnamed: L2.2, U10.6
unnamed: L3.1, L5.1, U13.12
unnamed: L3.2, L4.1, U13.13
unnamed: R1.1, R7.2, U3.10
unnamed: R1.2, R3.2, U1.T1
unnamed: R2.1, R8.2, U4.10
unnamed: R2.2, R4.2, U2.T1
unnamed: R5.1, R7.1, U1.B18
unnamed: R6.1, R8.1, U2.B18
unnamed: R10.1, R16.2, U8.10
unnamed: R10.2, R12.2, U6.T1
unnamed: R9.2, R11.2, U5.T1
unnamed: R13.1, R15.1, U5.B18
unnamed: R14.1, R16.1, U6.B18
unnamed: R9.1, R15.2, U7.10
unnamed: R17.2, U12.D14
unnamed: R21.2, R22.1, U10.5
unnamed: R23.2, U13.16
unnamed: R29.2, U16.8
VCC: C20.1, C23.1, C27.1, C30.1, C34.1, C40.1, C42.1, L2.1, R21.1, U10.4, U12.D6, U12.E4, U12.E11, U12.J11, U12.L4, U12.L9
VDD: C3.2, C4.2, C5.2, C6.2, C9.2, C10.2, C11.2, C12.2, C18.2, C19.1, C22.1, C25.1, C28.1, C32.1, C36.1, C41.1, C44.1, C45.1, L1.1, L6.2, R17.1, R18.2, R20.2, R25.2, R26.2, R27.2, R31.1, U3.13, U3.14, U3.15, U3.16, U3.26, U3.31, U4.13, U4.14, U4.15, U4.16, U4.26, U4.31, U7.13, U7.14, U7.15, U7.16, U7.26, U7.31, U8.13, U8.14, U8.15, U8.16, U8.26, U8.31, U12.A1, U12.B9, U12.C7, U12.C12, U12.D5, U12.D9, U12.F12, U12.G4, U12.J4, U12.J12, U12.L7, U12.L11, U12.N4, U12.P1, U12.P3, U14.4, U15.3, U15.7, U15.8

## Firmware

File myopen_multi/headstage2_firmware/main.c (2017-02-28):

#include <cdefBF532.h>
#include "headstage.h"
#include "nordic_regs.h"
#include "print.h"
#include "spi.h"
#include "usb.h"
#include "memory.h"

u32 g_excregs[8+6+16] ; //the regular data registers + pointer registers. 

void exception_report(unsigned long seqstat, unsigned long retx){
	//shift the bottom 5 bits out on portf 0 and 1 (1 = clock); 
	//radio may get a bit confused, but these are both inputs so it's ok
	unsigned long mask, out; 
	int i; 
	*pFIO_FLAG_D = 0; 
	printf_str("Exception!!"); 
	printf_hex("hwerr:", (seqstat >> 14) & 0x1f); 
	printf_hex("excause:", seqstat & 0x3f); 
	printf_hex("retx:", retx); 
	u32* p = g_excregs; 
	printf_hex("r0:", *p++); 
	printf_hex("r1:", *p++); 
	printf_hex("r2:", *p++); 
	printf_hex("r3:", *p++); 
	printf_hex("r4:", *p++); 
	printf_hex("r5:", *p++); 
	printf_hex("r6:", *p++); 
	printf_hex("r7:", *p++); 
	uart_str("\n"); 
	printf_hex("p0:", *p++); 
	printf_hex("p1:", *p++); 
	printf_hex("p2:", *p++); 
	printf_hex("p3:", *p++); 
	printf_hex("p4:", *p++); 
	printf_hex("p5:", *p++); 
	//loop registers. 
	uart_str("\n"); 
	printf_hex("i0:", *p++); 		
	printf_hex("b0:", *p++); 		
	printf_hex("l0:", *p++); 	
	uart_str("\n"); 
	printf_hex("i1:", *p++); 		
	printf_hex("b1:", *p++); 		
	printf_hex("l1:", *p++); 		
	uart_str("\n"); 
	printf_hex("i2:", *p++); 		
	printf_hex("b2:", *p++); 		
	printf_hex("l2:", *p++); 		
	uart_str("\n"); 
	printf_hex("i3:", *p++); 		
	printf_hex("b3:", *p++); 		
	printf_hex("l3:", *p++); 		
	uart_str("\n"); 
	printf_hex("m0:", *p++); 		
	printf_hex("m1:", *p++); 		
	printf_hex("m2:", *p++); 		
	printf_hex("m3:", *p++); 		
	while(1){
		//pulse pf 7 (MUX0) for trigger.
		*pFIO_FLAG_T = 0x100; 
		asm volatile("ssync"); 
		*pFIO_FLAG_T = 0x100; 
		asm volatile("ssync"); 
		
		mask = 0x20; 
		out = seqstat;
		for(i=0; i<6; i++){
			if(mask & out)
				*pFIO_FLAG_S = 1; 
			else
				*pFIO_FLAG_C = 1;
			*pFIO_FLAG_T = 2; 
			asm volatile("ssync"); 
			mask = mask >> 1; 
			*pFIO_FLAG_T = 2; 
			asm volatile("ssync"); 
		}
		*pFIO_FLAG_C = 1;
		// insert a pause. 
		for(i=0; i<30; i++){
			asm volatile("nop; nop;"); 
		}
		//only shift out the last 16 bits of retx - we know the top 16 bits. 
		mask = 0x8000; 
		out = retx;
		for(i=0; i<16; i++){
			if(mask & out)
				*pFIO_FLAG_S = 1; 
			else
				*pFIO_FLAG_C = 1;
			*pFIO_FLAG_T = 2; 
			asm volatile("ssync"); 
			mask = mask >> 1; 
			*pFIO_FLAG_T = 2; 
			asm volatile("ssync"); 
			//break into nibbles. (and format for the oscilloscope)
			if((i & 3) == 3){
				asm volatile("nop; nop; nop; nop; nop; nop; nop; nop;"); 
				asm volatile("nop; nop; nop; nop; nop; nop; nop; nop;"); 
				asm volatile("nop; nop; nop; nop; nop; nop; nop; nop;"); 
			}
		}
		*pFIO_FLAG_C = 1;
		// insert a pause. 
		for(i=0; i<300; i++){
			asm volatile("nop; nop;"); 
		}
	}
}

void nmi_report(void){
	int i; 
	printf_str("nonmaskable exception!"); 
	printf_str("this should not occur - hardware problems!"); 
	for(i=0; i<300; i++){
		asm volatile("nop; nop;"); 
	}
}

int main()
{
	u16 k; 
	
	//make sure cache is off.
	*pIMEM_CONTROL = 1;  
	asm volatile("csync"); 
    // DAG0 non-cacheable fetches use port A. Shouldn't really matter
	*pDMEM_CONTROL = 1; 
	asm volatile("csync"); 
	
	*pFIO_INEN = 0x8; // Enable PF3 as input - radio's _IRQ
	*pFIO_DIR = ~(*pFIO_INEN); // All other PF pins output
    // PF0=PF1=PF2=1: Nordic CE pin, Nordic CS deselect (active low), Flash CS deselect
	*pFIO_FLAG_D = 0x0187; 
	
	radio_init(124);      // radio channel, match with what gtkclient expects 
	*FIO_CLEAR = SPI_CE; // CE on radio 
	*FIO_CLEAR = 0x0080; //Clear PF3 - captured state from NRF-IRQ
	for(k=0; k<1000; k++){
		asm volatile("nop; nop; nop; nop;"); 	
	}
	
	radio_set_tx();
    // First disable all SPORT
    *pSPORT0_TCR1 = 0x0000;
    *pSPORT0_RCR1 = 0x0000;
    *pSPORT1_TCR1 = 0x0000;
    *pSPORT1_RCR1 = 0x0000;
    
    /* SCLK = 80MHz
     * TSCLKDIV = 1
     * TSCLK = SCLK / 2*(TSCLKDIV+1) = 80Mhz/4 = 20Mhz. Period = 50ns
     * TFS is active low
     * TFSDiv = 3 --> TFS is pulsed high for 3+1=4 cycles = 200ns. This
     *                seres as _CS for Intan (min=154ns).
     *
     * Receive serial clock RSCLK is connected to TSCLK - IRCLK=0
     * Receive frame sync RFS is externally generated through connection from
     * TFS - IRFS = 0
     *
     * Both Receive and Transmit use late-frame sync - LATFS = 1
     *
     * TCKFE = 1: Transmit drive data and internal frame-syncs with falling edge of TSCLK.
     * RCKFE = 1: Rising RSCLK/TSCLK edge to sample data and externally generated frame sync.
     */

    // Using TSCLK for late-frame-sync
    // SPORT0 transmit
    *pSPORT0_TCLKDIV = 1;
    *pSPORT0_TFSDIV = 3;
    *pSPORT0_TCR2 = TXSE | 0x10; // allow secondary; 

    // SPORT1 transmit
    *pSPORT1_TCLKDIV = 1;
    *pSPORT1_TFSDIV = 3;
    *pSPORT1_TCR2 = TXSE | 0x10; // allow secondary;

    // SPORT0 receive
    // Serial clock and frame syncs derived from TSCLK and TFS, so RCLKDIV and RFSDIV ignored.
    *pSPORT0_RCR2 = RXSE | 0x10; // allow secondary; 

    // SPORT1 receive
    // Serial clock and frame syncs derived from TSCLK and TFS, so RCLKDIV and RFSDIV ignored.
    *pSPORT1_RCR2 = RXSE | 0x10;

    /* Using RSCLK for late-frame-sync
    *pSPORT0_RCLKDIV = 1;
    *pSPORT0_RFSDIV = 4;
    *pSPORT0_RCR2 = RXSE | 0xf;

    *pSPORT1_RCLKDIV = 1;
    *pSPORT1_RFSDIV = 4;
    *pSPORT1_RCR2 = RXSE | 0xf;

    *pSPORT0_TCR2 = TXSE | 0xf;
    *pSPORT1_TCR2 = TXSE | 0xf;
    */

    // TSCLK for early-frame-sync
    /*
    *pSPORT0_TCLKDIV = 1;
    *pSPORT0_TFSDIV = 19;
    *pSPORT0_TCR2 = TXSE | 0xf;

    *pSPORT1_TCLKDIV = 1;
    *pSPORT1_TFSDIV = 19;
    *pSPORT1_TCR2 = TXSE | 0xf;

    *pSPORT0_RCR2 = RXSE | 0xf;
    *pSPORT1_RCR2 = RXSE | 0xf;
    */

    //---- block from Tim firmware-----
    //*pSPORT0_RCLKDIV = 1; //Determines the SCLK frequency and hence the data bit rate
	//*pSPORT0_RFSDIV = 19; //number of clock cycles -1 before generating TFS pulse. 
	//*pSPORT0_RCR2 = 0x010f; //16 bit word, secondary channel enabled, no stereo. 
	
	//*pSPORT1_RCLKDIV = 1; //Determines the SCLK frequency and hence the data bit rate
	//*pSPORT1_RFSDIV = 19; //number of clock cycles -1 before generating TFS pulse. 
	//*pSPORT1_RCR2 = 0x010f; //16 bit word, secondary channel enabled, no stereo. 
    //---- Tim block end -------------
    

    //------------ Testing Frame Syncs only ----------
    *pSPORT0_TCR1 = TCKFE | LATFS | LTFS | TFSR | ITFS | ITCLK | DITFS;
    *pSPORT1_TCR1 = TCKFE | LATFS | LTFS | TFSR | ITFS | ITCLK | DITFS;
    *pSPORT0_RCR1 = RCKFE | LARFS | LRFS | RFSR;
    *pSPORT1_RCR1 = RCKFE | LARFS | LRFS | RFSR;
    
    asm volatile("ssync;");
    /* 
    *pSPORT0_TCR1 = TCKFE | LATFS | LTFS | TFSR | ITFS | ITCLK | TSPEN;// | DITFS;
    *pSPORT1_TCR1 = TCKFE | LATFS | LTFS | TFSR | ITFS | ITCLK | TSPEN;// | DITFS;
    *pSPORT0_RCR1 = RCKFE | LARFS | LRFS | RFSR | RSPEN;
    *pSPORT1_RCR1 = RCKFE | LARFS | LRFS | RFSR | RSPEN;

    asm volatile("ssync;");
    */
    
    radio_bidi_asm(); //infinite loop! ends here!
    
    /*
    while (1) {
        asm volatile("nop;");
    }
    */
	return 0;
}

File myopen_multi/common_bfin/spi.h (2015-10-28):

#ifndef __SPI_H__
#define __SPI_H__

#ifdef __ADSPBF532__
//need to define the SPI pins, etc.
#ifndef __ASM__
#include <cdefBF532.h>
#endif

#define FIO_CLEAR		pFIO_FLAG_C
#define FIO_SET		    pFIO_FLAG_S
#define FIO_TOGGLE	    pFIO_FLAG_T
#define FIO_IN			pFIO_FLAG_D
#define FIO__INEN		pFIO_INEN
#define FIO__DIR		pFIO_DIR

#define USB_SS 		0x0040 //pin 6 on port F (and 7 on broken board XXX)
#define USB_IRQ 		0x0010 //pin 4 on port F
#define USB_RESET 	0x0800 //pin 11.

//SPI pins.
#define SPI_IRQ	 	0x0008
#define SPI_CSN		0x0002
#define SPI_CE		0x0001

#ifdef __BRIDGE__
#define SPI_BAUDDIV 5 //stimulator/bridge
#else
#define SPI_BAUDDIV 4 //headstage.  4->10Mhz, looks oaky (not okay, oaky)
#endif

#endif

#ifdef __ADSPBF537__
#include <cdefBF537.h>

#define FIO_CLEAR		pPORTFIO_CLEAR
#define FIO_SET		    pPORTFIO_SET
#define FIO_TOGGLE	    pPORTFIO_TOGGLE
#define FIO_IN			pPORTFIO
#define FIO__INEN		pPORTFIO_INEN
#define FIO__DIR		pPORTFIO_DIR

#define USB_SS 0x4000 //on port F.
#define USB_IRQ 0x0100

//SPI pins, needed by spi.c
#define SPI_IRQ	0x4000 //port f pin 14
#define SPI_CSN	0x0010 //port f pin 4
#define SPI_CE	0x0020 //port f pin 5

#define SPI_BAUDDIV 11

#endif

#ifdef __ADSPBF527__
#include <cdefBF527.h>

#define FIO_CLEAR		pPORTGIO_CLEAR
#define FIO_SET		pPORTGIO_SET
#define FIO_TOGGLE	pPORTGIO_TOGGLE
#define FIO_IN			pPORTGIO
#define FIO__INEN		pPORTGIO_INEN
#define FIO__DIR		pPORTGIO_DIR

//SPI pins, needed by spi.c
#define SPI_IRQ	0x0800 //port G pin 11
#define SPI_CSN	0x0200 //port G pin 9
#define SPI_CE		0x0400 //port G pin 10
#define SPI_FLASH	0x0002 //port G pin 1

#define SPI_BAUDDIV 6
// system clock is 125Mhz, so divide by 12. (10.41MHz)

#endif

#ifndef u8
#define u8 unsigned char
#endif
#ifndef u16
#define u16 unsigned short
#endif

#ifdef __BLACKFIN__
	#ifndef u32
	#define u32 unsigned long
	#endif
#else
	#ifndef u32
	#define u32 unsigned int
	#endif
#endif

// SPI routines.
#ifndef __ASM__
void spi_delay();
u8 spi_write_register(u8 reg, u8 val);
u8 spi_write_register_ver(u8 reg, u8 val);
u8 spi_read_register(u8 reg);
u8 spi_read_register_status(u8 reg, u8* value);
u8 spi_write_byte(u8 byte);
void spi_write_packet(void* packet);
void spi_write_packet_noDMA(void* packet);
int spi_read_packet(void* packet);
void spi_read_packet_nocheck(void* packet);
void radio_set_rx();
void radio_set_tx();
int radio_wait_irq(int time);
u8 radio_init(u8 chan);

void udelay(int us);
void printf_newline();
#endif
#endif

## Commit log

2015-05-11 First commit. All the relevant parts of the wireless system.
    [analog.sch, audioout.sch, poe.sch, stage10-Back.gbl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]
2015-05-11 The actual wireless system stuff was in the "multi" branch of the myopen project which was not migrated to Tim's github repo. So I delete those ones.
    [analog.sch, audioout.sch, poe.sch, stage10-Back.gbl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]
2015-05-11 Included the correct gtkclient_multi from myopen_multi with all the firmwares. (Not sure what stage6 is). Changed the names of the firmware to match their contents. Added Pohe's Makefile for gtkclien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
    [analog.sch, audioout.sch, poe.sch, stage10-Back.gbl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]
2015-05-18 Editing gtcklient.cpp for threading and bridge binding issues.
2015-06-07 Started designing the headstage using 4 RHD2132 Intan chips. Need to interface with SPORTs instead of SPIs, like before.
    Cleaned up some code.
    [analog.sch, headstage2.sch, stage9.sch]
2015-07-06 Organized changes. Converted the old kicad projects. Started 4xRHD2132 headstage version. Recompiled gtkclient_multi for Ubuntu and newer protobufs.
    [analog.sch, headstage2.kicad_pcb, headstage2.sch, stage9.sch]
2015-07-06 Screwed up the old kicad project files again by saving the board file. NEVER SAVE OLD .BRD FILES!!!
    Fixed this and updated README with instructions to port old kicad
    projects.
    [analog.sch, stage9.sch]
2015-07-10 Finished PCB layout, generated Gerber passed freedfm.com online check.
    [headstage2-B_Cu.gbl, headstage2-B_Mask.gbs, headstage2-B_SilkS.gbo, headstage2-Edge_Cuts.gbr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]
2015-08-28 Headstage2_hardware gerber gtkclient.cpp
    [headstage2.kicad_pcb, headstage2.sch]
2015-09-22 Ported flash.c to python using PyParallel for programming the flash memories. This is because libparapin doesn't work for Ubuntu 14.04. Probably because libparapin was last made to work with linux ke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
    Makefiles in headstage_firmware and bridge_firmware changed so "make
    flash" invokes the new flash.py.
    [headstage2_bom.csv]
2015-09-26 Tried to modify Makefile to get JTAG debugging via gnICE to work with headstage...wrongly detect the DSP as BF533. Error of "Cannot find bounds of current function".
2015-10-20 Went through all of the firmware, made more complete comments on the code.
    Things still not very clear to me:
    * The LMS algorithm update, the variable gain vs. the fixed gain of 3.
    * How is the timing for radio-transmission and waitIRQ calculated? Need
    to count signal path length. Seems to be greater than the 4ms PLL
    free-run time...
    * How are the channels updated in gtkclient? -- where does this happen
    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
    [memory_map.ods]
2015-10-28 Started writing Headstage2 firmware. Changes mostly in headstage2_firmware/firmware.asm's initialization code regarding SPORTs, to get the BFin to play well with Intans.
    [Intan_setup.ods, headstage2.sch, memory_map.ods]
2015-10-29 Wrote code and comment documenation for headstage2's signal chain for the first pair of samples.
    [memory_map.ods]
2015-10-30 Found a mistake!!! My LED pad was put on the board backwards...the LED will always be reverse biased and not light up!
    I've fixed this by changing the footprint associated with the LED,
    changed the footprint on the PCB file, and updated the gerber and drill
    file and SMD position files.
    [headstage2-B_Cu.gbl, headstage2-B_Mask.gbs, headstage2-B_SilkS.gbo, headstage2-Edge_Cuts.gbr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]
2015-11-12 Problems with using SPORT as SPI to communicate to RHD2132 are still unresolved.
    frame_sync_test.asm used as a minimal test to understand how frame-sync
    works.
    firmware1.asm is the current file where I test different ways. Still
    have to investigate how the signal chain needs to be changed.
    [Intan_setup.ods, headstage2.sch]
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2015-11-13 Used JTAG debug to check if I'm actually reading correctly when sending commands to read Intan reg40-44 in order.
    It looks good!! Setting used is TFSDIV=3, 17 bits data length, DITFS,
    late frame sync.
    One thing to realize is that framesync might not work properly for the
    first three cycles -- i.e. after SPORTs are enabled, the first two
    results received are crap. The third one corresponds to the first
    command sent to Intan..2 out of the 4 results are simply 0's. This is
    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
    [memory_map.ods]
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2015-11-16 Test results: Changing CONVERT(63) to CONVERT(0), CONVERT(1),... does not fix the noisy result when polling each amplifier channel in turn. Increasing _CS duration also doesn't fix it.
    The only violation I have left is the enable lag time, which I cannot
    fulfill simultaneously with enable lead time if I'm using SPORT. This is
    likely the culprit and I can't think of a way to fix it...
    [Intan_setup.ods]
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2015-11-20 Editted the official firmware.asm file.
    To make it easier to compare, I'm taking the 16-bit ADC result and down
    shifting it to 12-bits, thus allowing me to use Tim's signal chain code
    as is.
    Intan-setup include the DSP-offset. However, this doesn't seem to
    mitigate the noise problem I see on the board. Need to figure out if
    this is due to a more noisy board layout, or software problem
    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
    [memory_map.ods]
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2015-12-08 Started writing the basic firmware that transmits only raw samples through radio, in radio_basic.asm
    radio_basic_memoryMap contains the new memory map. Only W1 is changed.
    All the other buffers will either be 0 or not used/irrelevant.
    This is reflected in the addition of memory_radio_basic.h, which changes
    W1_STRIDE, etc. Also, changed radio_bidi_asm's assignment of circular
    buffer pointers. The math should pretty much stays the same, given
    W1_STRIDE changes.
    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
    [memory_map.ods, radio_basic_memoryMap.ods]
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2015-12-18 Implemented AGC in radio_AGC.asm, like Tim's version. Also modified gtkclient to work with signal-chain = AGC.
    Does not work for some reason, AGC is not responding. Going to try my
    own implementation to see if it works. Commit so I can revert later.
    [radio_AGC_memoryMap.ods]
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2015-12-23 I think I finally understand how the AGC code works and why I couldn't get it work before.
    The key is, the AGC gain works only on the deviation of the signal from
    the integrated mean. The integrated mean is updated through the
    integrator-highpass stage, which I decided to throw away. Since I don't
    have access to the integrated mean from the Intan, I will need to
    implement this stage after all.
    This required adding in extra memory items in W1 - for holding the
    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
    [radio_AGC_memoryMap.ods]
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2016-01-12 Implemented IIR filter - two biquads, bandpass from 500Hz to 9kHz.
    Investigating what is wrong with the signal corruption. Made oscillator
    test to generate oscillations by changing IIR filter coefficients..this
    is almost done.
    Finally, changed the Makefile, so the build process involving protobufs
    is a lot easier and straight forward. Shouldn't encounter too many
    protobuf problems when others download it onto a fresh system.
    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
    [radio_AGC_IIR_memoryMap.ods, radio_AGC_memoryMap.ods]
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2016-01-15 Started the final firmware radio_all.asm Made radio_all_memoryMap.ods. Discovered headstage_firmware's memoryMap.ods had errors in it (aperture memory), corrected now.
    [memory_map.ods, radio_all_memoryMap.ods]
2016-01-17 Finished writing firmware with SAA spike sorting included. Also added the corresponding changes in gtkclient.
    Made all files include "memory.h", but copy different firmware's
    memory header files to that name when doing "make clean"...this needs to
    go in README.
    radio_AGC_IIR_SAA.asm still suffers from the same radio-transmission
    caused data corruption. But I'm not able to find anything that might
    cause it...at this point, the pkt-assembly code is exactly the same as
    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
    [memory_map.ods, radio_all_memoryMap.ods]
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2016-01-21 Added the spreadsheets too
    [RHA_RHD_electrodes_matching.ods]
2016-01-21 Fixed typos in headstage.cpp
    [analog.sch, headstage2.sch]
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2016-03-11 Start finalizing validation of the wireless system.
    Matlab files in gtkclient_multi/ mostly for processing gtkclient saved
    files and analyzing performance.
    Also wrote another version of RHD firmware - radio_gain_IIR_SAA, where
    instead of AGC, a fixed Q7.8 gain is applied, configurable within
    gtkclient.
    Also, discovered that the hardware filters on Intan might be distorting
    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
    [radio_all_memoryMap.ods, radio_gain_IIR_SAA_memoryMap.ods]
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2017-07-23 Implemented LMS. 1) Tested that with the Intan acquisition trick, I can indeed squeeze in extra cycles, in both radio_AGC_IIR_SAA.asm and radio_gain_IIR_SAA.asm 2) Added LMS into radio_AGC_IIR_SAA.as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
    1) Implement invertable gain by changing the IIR coefficients.
    2) Can the IIR gain still be changed after going through LMS?
    3) Test on monkey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
    [memory_map.ods, radio_AGC_IIR_SAA_memoryMap.ods, radio_AGC_LMS_IIR_SAA_memoryMap.ods, radio_all_memoryMap.ods]
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

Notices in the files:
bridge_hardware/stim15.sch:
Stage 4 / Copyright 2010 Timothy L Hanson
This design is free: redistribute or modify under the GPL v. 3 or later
